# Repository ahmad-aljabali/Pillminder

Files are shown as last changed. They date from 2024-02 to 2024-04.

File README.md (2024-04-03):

# Pillminder
Medication Dispenser and Tracker App. [Download apk](Build/Pillwise.apk)

# Table of Contents
1. [Introduction](#introduction)
2. [Design](#design)
1. [Hardware](#hardware)
2. [Electronics](#electronics)
3. [Mobile App](#app)
3. [Building the App](#building)
4. [Issues and Challenges](#issues)
5. [Conclusion & Future Works](#conclusion)
6. [References](#references)

# Introduction 
In this project, our aim was to develop an inventive solution for monitoring and managing resources vital to an individual's well-being, with a specific focus on medications. Our initial market research highlighted areas for improvement in existing solutions.

We observed that available products in the market were either exclusively app-based or hardware-based. The existing dispensers were often proprietary, offering limited customization options, featuring bulky designs, and were not tailored to meet the needs of individual users.

To address these shortcomings, we chose a dual-component approach for our project: a smart pill dispenser and a companion mobile app designed for medication tracking. Our vision was to create a comprehensive product that could function both independently and in sync with each other. This design allowed users the flexibility to use the dispenser on its own or utilize the app solely as a medication reminder. By providing this dual functionality, our aim was to offer a flexible and user-friendly solution, catering to a diverse range of user preferences and needs.

## Videos

https://github.com/ahmad-aljabali/Pillwise/assets/36141448/d999e439-b2e4-46c4-b8eb-4feb8e34578a

https://github.com/ahmad-aljabali/Pillwise/assets/36141448/cecf2776-79e3-4c20-b9d0-7685703d312a 

# Design 

## Hardware 
The aim was to create a simple and compact design that can be placed and used easily. The design incorporated a rotating plate capable of storing multiple medications, facilitating dispensing according to the prescription. To enhance user interaction, a visual display feature was integrated to notify users of medication times and provide instructions.

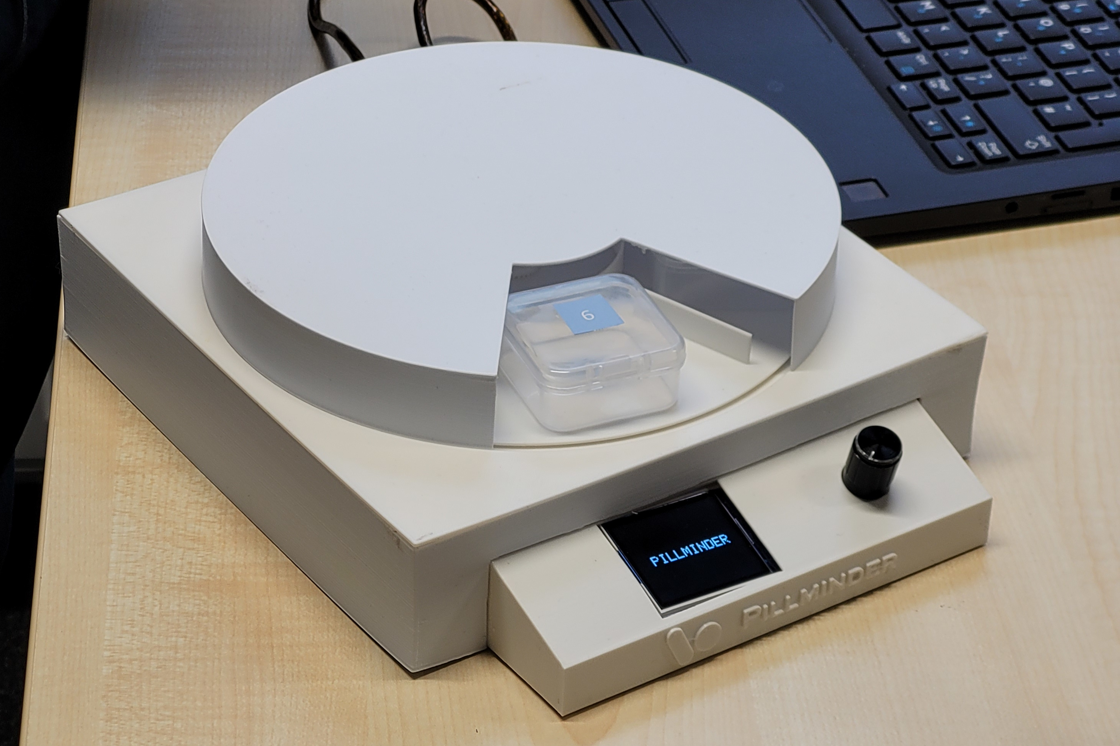
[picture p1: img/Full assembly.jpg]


### 3D Modeling & Printing
The design process was accomplished by:

- Measure the dimensions of the main components so we can build a model that fits all the components and maintains a compact size. Precise measurements were obtained using a digital caliper.

- Using Autodesk Inventor Professional, we created detailed 3D models for each part of the prototype. This design process accounted for the dispenser's functionality, accommodating six types of medication on a rotating plate.

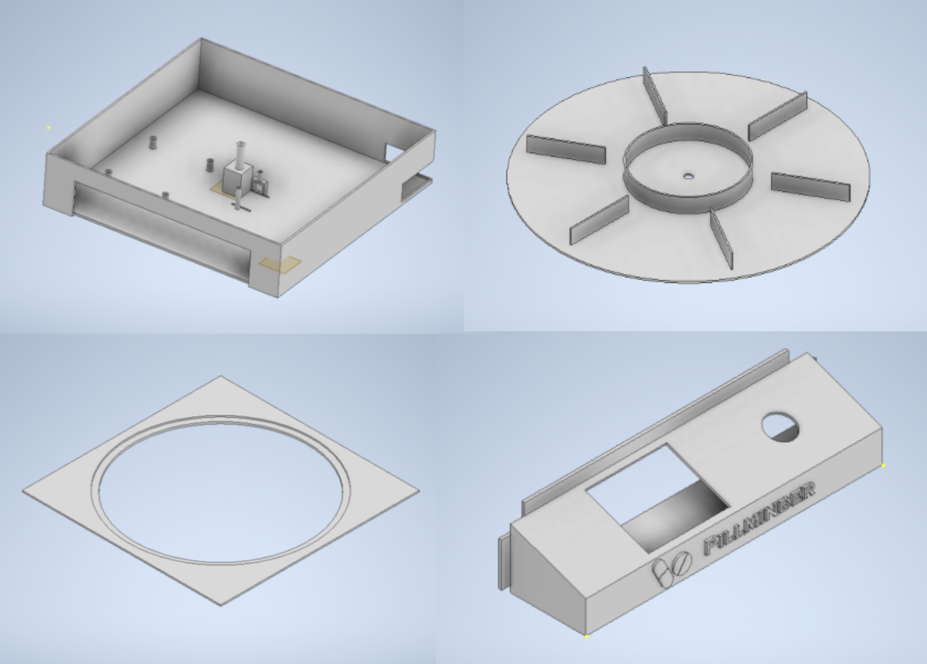
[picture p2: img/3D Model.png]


- The next step involved bringing our 3D models to life. We utilized a Prusa i3 MK3S+ FDM printer, with a slicing size set at 0.2-0.3 mm. The final printed dimensions of the prototype were 21 x 21 x 25 cm.

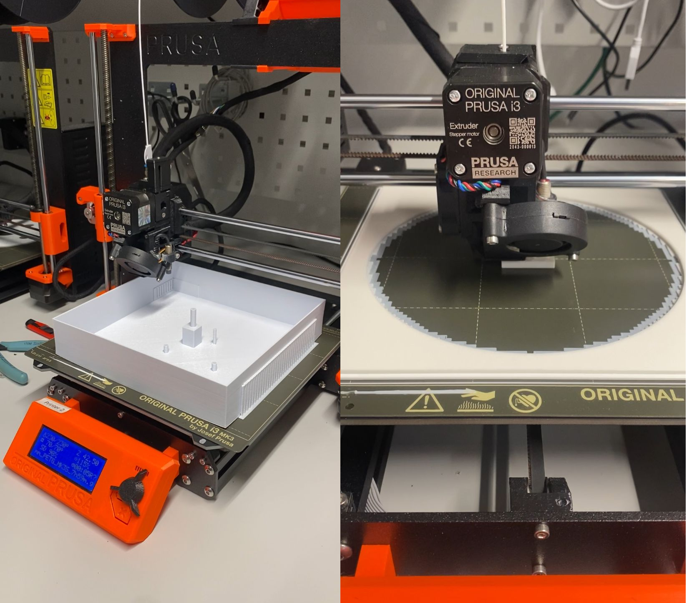
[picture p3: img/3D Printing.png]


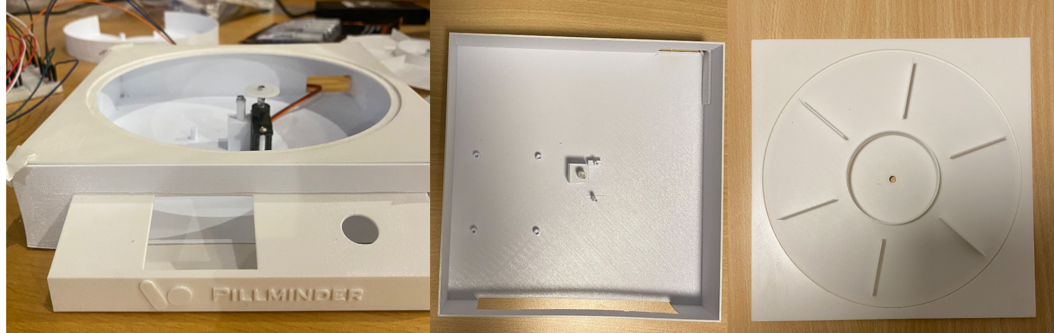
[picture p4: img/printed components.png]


## Electronics 
In this section, we will write in detail about the electronic components that are the core of our prototype. To achieve the goal of creating an automated prototype, we used an Arduino Uno microcontroller as the central processing unit. To establish a connection between the Arduino Uno and our mobile application, we integrated the ESP8266-01 Wi-Fi module. This module served as the communication bridge, enabling real-time interaction between the prototype and the user through the mobile app.

### Electronic Component:
- Arduino Uno
- WiFi ESP8266-01S
- Servo Motor MF-90
- Rotary Encoder KY-040
- LCD 1.8" TFT Display ST7735S
- Wires & Breadboard

After having every component , we started to verified the functionality of them before integrating into the overall electronic system.

https://github.com/ahmad-aljabali/Pillwise/assets/36141448/dc6bbddc-dbca-42d1-aa9b-e82a9cc1dbc5

## Mobile App 
### Architecture & Libraries
The app was develop with the goal of being usable as a standalone medicine tracking mobile app and/or in combination with the Dispenser.

Another design consideration was to use cross platform technologies, we settled in the end on using React single page PWA framework because of our prior familiarity with web development, this was used in combination with Ionic and Capacitor to add native app functionality.

For management of native functionality the following capacitor add-ons were utilized:
- Filesystem[^5]: for storing and reading user data locally 
- Local Notification[^6]: to provide push notification to user

For ease of development and quick modification the user data is stored in JSON format instead of using a dedicated database, saved in the standard native Android file structure.

### Layout
The app is split into three main screens, each displaying the following.
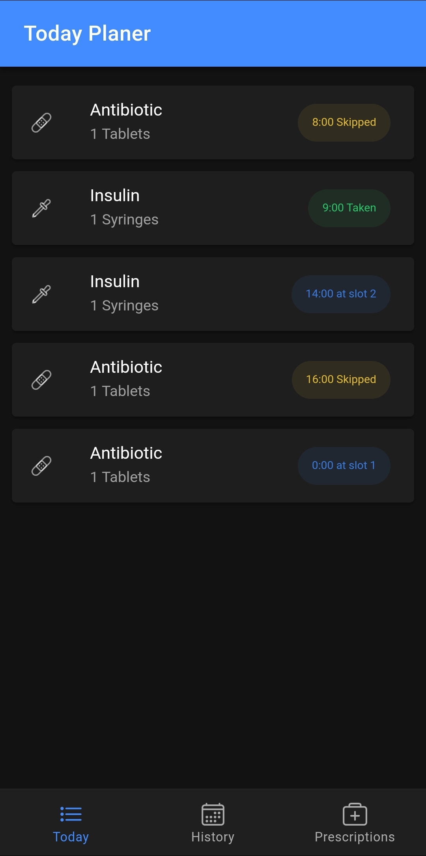
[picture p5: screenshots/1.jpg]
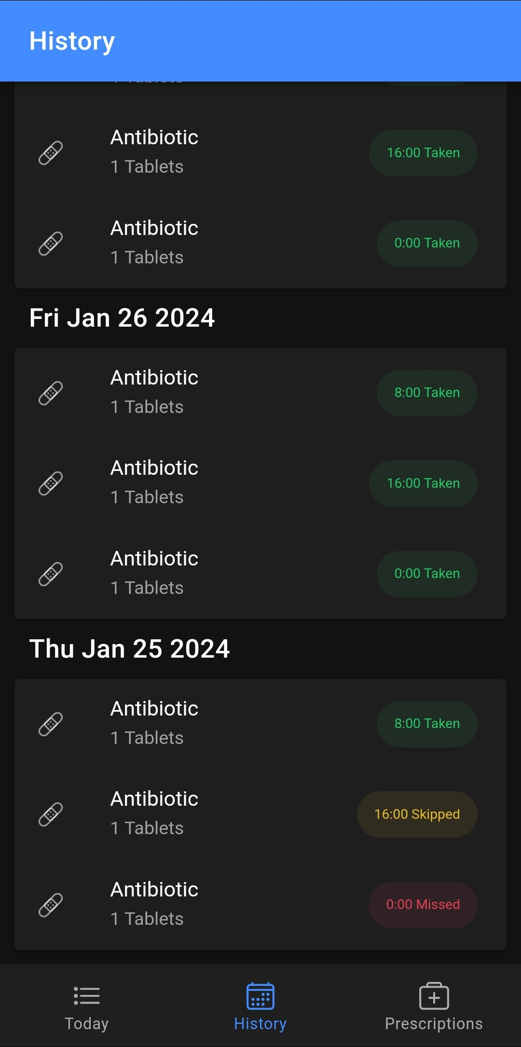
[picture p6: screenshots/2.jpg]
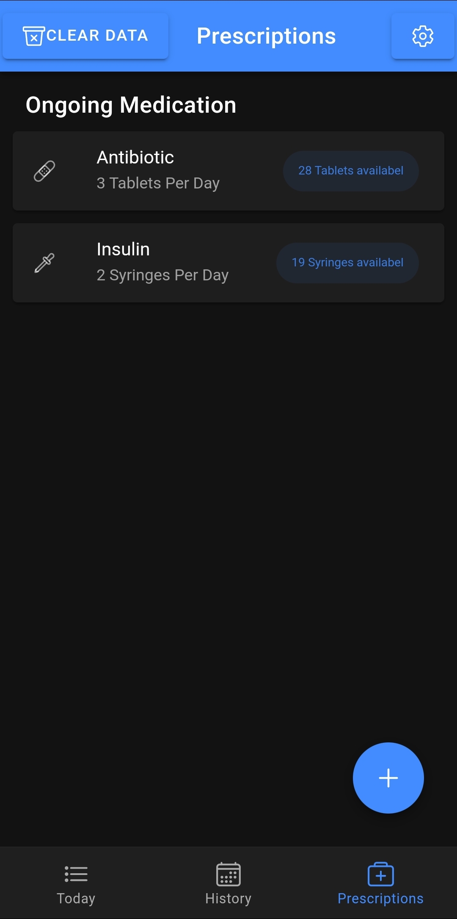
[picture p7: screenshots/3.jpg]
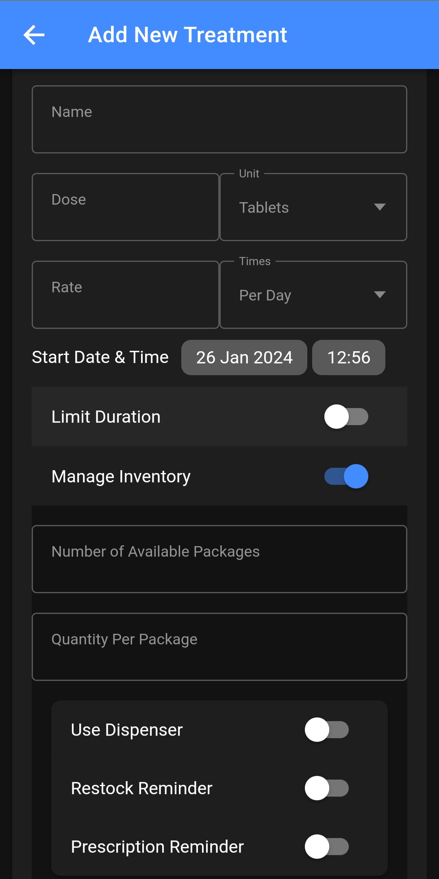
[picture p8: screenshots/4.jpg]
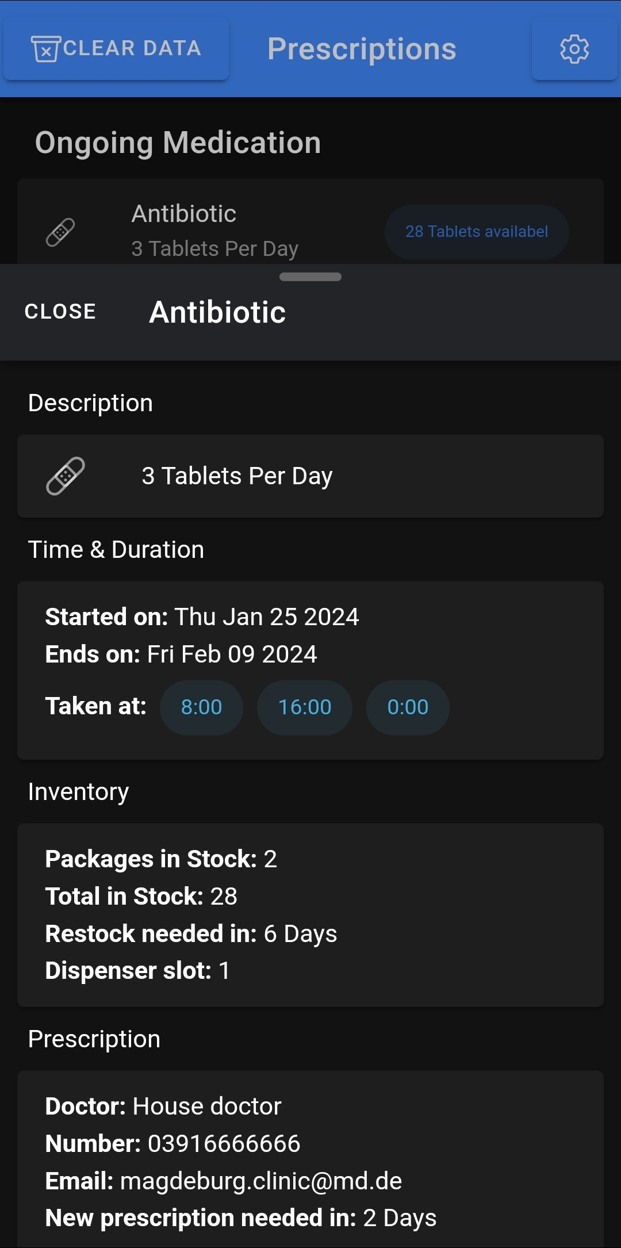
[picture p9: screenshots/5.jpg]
||||
---|---|---|---|---

**Today**
- Medication Name, Dose, Type
- Times to be taken today
- Slot if they're stored in Dispenser
- Allow user to Confirm or Skip medicine

**History**
- Status Record of Medication in previous days

**Prescriptions**
- Active Prescriptions
- Current stock value
- Button to add new prescription

Additionally the following screens are available.

**Add New Treatment**
- Form to Add New Medication
- Name, Dose, Type, Rate, Start Date & Time
- Inventory Info
- Prescription and Doctor Info

**Medicine Details**
- Can be accessed by clicking on Medication in Prescriptions Screen
- Shows complete medication info

# Building the App 
To build the App from the available source code [^7] use the below instructions.

### Install Dependencies
```
npm install
```

### Run locally
```
ionic serve
```
### Build for android
```
ionic cap add android
ionic cap build android
```
**_Then build using android studio_**
**_Replace android with ios and use Xcode to build for ios_**

# Issues and Challanges 

## 3D Printing

The 3D printer's dimensions posed a challenge as they were smaller than the model dimensions. Consequently, we divided the case into two parts one for internal components and another for the LCD and encoder. 

Securing all components proved challenging, especially when considering the rotating plate where precision was crucial. The plate needed to be affixed with a glued gear, ensuring contact with the servo but not overly tight. Excessive tightness could hinder the servo motor's smooth rotation, leading to potential interruptions. 

Addressing this challenge would require creating a new model with more accurate dimensions and improved fixation points, resolving potential issues related to plate movement and servo rotation.

However, due to time limitations and restricted access to the printing lab, this optimization was not implemented.

## Electronics

Our initial microcontroller choice was Raspberry Pi, because of its communication capabilities and the ease of hosting a local server.

Unfortunately, the Raspberry Pi unexpectedly ceased functioning, causing the need for an alternative solution. The simplest idea was to buy another Raspberry Pi, but out limited budget led us to look for a more affordable solution. Since most of us were familiar with Arduino Uno, we decided to use it as our microcontroller. 

We knew that Arduino Uno does not have built-in Wi-Fi, we solved this limitation by adding the ESP8266-01 module. This decision was influenced by the compact size of the ESP8266-01, which fit with the dimensions of our pre-existing 3D printed model. Despite the ESP8266-01's benefits, we faced some challenges due to its basic low level functionality, forcing us to use "_AT Commands_" instead of standard libraries. 

This method worked well, but it required a lot of effort to handel and parse incoming command, due to lack of libraries to handel requests for this module.

# Conclusion & Future Works 
Our project began with a basic idea: creating a prototype for a medical dispenser paired with a mobile app. We simultaneously worked on prototyping, 3D modeling, Arduino Uno code, and mobile app. Despite facing various challenges, we successfully integrated the dispenser prototype with the mobile app, simplifying medication tracking for users.

Looking ahead, the design may be improved by enhancing user-friendliness. This involves implementing a database of nearby pharmacies with specific medicines and introducing a scanning feature for users to easily input medication details into the app. These improvements will provide users with a more intuitive and efficient medication management experience.

# References 
[^1]: https://www.electronics-lab.com/project/using-st7735-1-8-color-tft-display-arduino/
[^2]: https://gndtovcc.home.blog/2020/02/11/code-for-obtaining-ip-address-from-esp-01/
[^3]: https://www.makerguides.com/servo-arduino-tutorial/
[^4]: https://www.diyengineers.com/2021/06/03/arduino-rotary-encoder-how-to-use/
[^5]: https://capacitorjs.com/docs/apis/filesystem
[^6]: https://capacitorjs.com/docs/apis/local-notifications
[^7]: https://github.com/ahmad-aljabali/Pillwise/tree/main/App%20src%20code

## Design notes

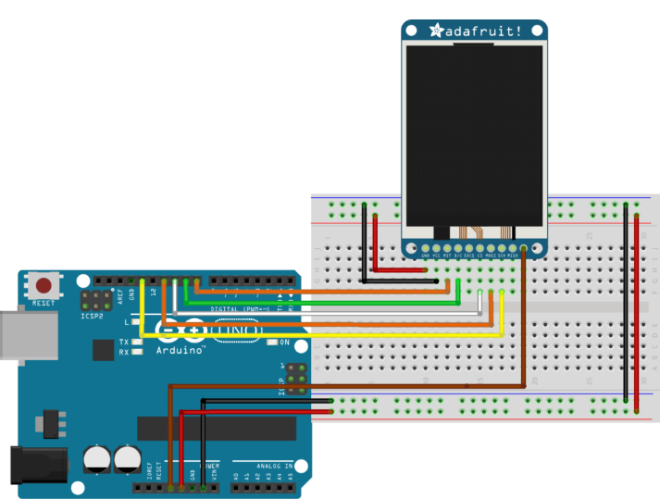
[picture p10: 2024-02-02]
img/image.png

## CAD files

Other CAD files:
3D Models/Box cover.ipt
3D Models/Box.ipt
3D Models/Plate cover.ipt
3D Models/Rotating Plate.ipt
3D Models/Screen1.ipt

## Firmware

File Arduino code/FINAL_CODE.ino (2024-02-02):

#include <SPI.h>
#include <Adafruit_GFX.h>
#include <Adafruit_ST7735.h>
#include <Servo.h>
#include <SoftwareSerial.h>

Adafruit_ST7735 tft = Adafruit_ST7735(10, 9, 8); // (CS, DC, RST)
Servo myservo;

#define encoderOutA 6 // CLK pin of Rotary Encoder
#define encoderOutB 7 // DT pin of Rotary Encoder
#define buttonPin 5    // Push-button pin
#define servoPin 4    // Servo control pin

SoftwareSerial ESP8266(3, 2);
const int arraySlot[7] = {80,93, 108, 123, 138, 153,180};
String names[7];
unsigned char times_check=0;
unsigned char check_connection=0;  
int counter ;// shife
int presentState;
int previousState;
int lastButtonState = HIGH;
int buttonState;
unsigned long lastDebounceTime = 0;
unsigned long debounceDelay = 50;
bool medicineTaken = false;
bool medicinePutted = false;
int i;
String secondValueName="";
String espData = "";
int slotValue=-1;
int typeValue;
void setup() {
  Serial.print(arraySlot[1]);
  pinMode(encoderOutA, INPUT);
  pinMode(encoderOutB, INPUT);
  pinMode(buttonPin, INPUT_PULLUP); // Enable internal pull-up resistor for the button pin

  myservo.attach(servoPin);

  tft.initR(INITR_GREENTAB);
  tft.setRotation(1);

  Serial.begin(115200);
  ESP8266.begin(115200);
  Serial.println("rjeu");
ESP8266.print("***VER:");
delay(2000);
ESP8266.println("AT+RST");
delay(3000);
ESP8266.println("AT+CWQAP");
delay(1000);
ESP8266.println("AT+GMR");
delay(1000);
ESP8266.println("AT+CWMODE=3");
delay(1000);
ESP8266.println("AT+CWLAP");
delay(3000);
ESP8266.println("AT+CIPMUX=1"); // Set multiple connections mode
delay(1000);
ESP8266.println("AT+CIPSERVER=1,80");
delay(10000);
Serial.println("Connecting to Wifi");
ESP8266.print("AT+CWJAP=\"Klevis\",\"klevis2023\"\r\n");
delay(10000);
     

 // setupESP8266();

  previousState = digitalRead(encoderOutA);
  //Serial.print(previousState);// just to see what print in beging 
}

void loop() {
  handleEsp8266();
  moveEncoder();
  checkButton();
  
}

void connectToWifi() {
  Serial.println("Connecting to Wifi");
while(check_connection==0)
  {
    Serial.print(".");
    ESP8266.print("AT+CWJAP=\"Klevis\",\"klevis2023\"\r\n");
    ESP8266.setTimeout(5000);
     if(ESP8266.find("WIFI CONNECTED\r\n")==1)
      {
      Serial.println("WIFI CONNECTED");
      int variabbb=1;
      break;}
      times_check++;
     if(times_check>3) {
      times_check=0;
      Serial.println("Trying to Reconnect..");}
}}





void setupESP8266() {
  ESP8266.println("AT+CIPMUX=1"); // Set multiple connections mode
  delay(1000);
  ESP8266.println("AT+CIPSERVER=1,80");
  delay(1000);
}

void handleEsp8266() {
  while (ESP8266.available()) {
    char c = ESP8266.read();
    espData += c;
    //Serial.print(espData);
    if (c == '\n') {
      String result = extractSubstring(espData, ":GET /", "2520");
      if (result.length() > 0) {
        String firstValueType = extractSubstring(result, "?type=", "$");
        secondValueName = extractSubstring(result, "$name=", "&");
        String thirdValueSlot = extractSubstring(result, "&slot=", "%");

        Serial.println("Received Values:");
        Serial.println("Type: " + firstValueType);
        Serial.println("Name: " + secondValueName);
        Serial.println("Slot: " + thirdValueSlot);
        slotValue = thirdValueSlot.toInt();
        typeValue=firstValueType.toInt();
        names[slotValue]=secondValueName;

        espData = "";
        firstValueType = "";
        secondValueName = "";
        thirdValueSlot = "";
        result = "";
        //slotValue=-1;
      }
    } 
    /*
    else {
      espData += c;
    }*/
  }
}

void moveServoBasedOnSlot(int slotValue) {
  // Implement your servo movement logic based on the slot value
  int angle = map(slotValue, 0, 100, 0, 180); // Adjust the mapping as needed
  myservo.write(angle);
  delay(500); // Adjust delay as needed
}

void printToLCD(String message) {
  tft.fillScreen(ST77XX_BLACK);
  tft.setCursor(10, 20);
  tft.setTextSize(2);
  tft.setTextColor(ST77XX_WHITE);
  tft.print("Name: ");
  tft.print(message);
}

String extractSubstring(const String &input, const String &startKeyword, const String &endKeyword) {
  int startIndex = input.indexOf(startKeyword);
  int endIndex = input.indexOf(endKeyword, startIndex + startKeyword.length());

  if (startIndex != -1 && endIndex != -1) {
    return input.substring(startIndex + startKeyword.length(), endIndex);
  } else {
    return ""; // Return an empty string if either start or end keyword is not found
  }
}

void checkButton() {
  int reading = digitalRead(buttonPin);

  if (reading != lastButtonState) {
    lastDebounceTime = millis();
  }

  if ((millis() - lastDebounceTime) > debounceDelay) {
    if (reading != buttonState) {
      buttonState = reading;

      if (buttonState == LOW  && slotValue==-1) {
        tft.fillScreen(0);
        tft.setCursor(50,60);
        tft.print("WAIT");
        servo_Slot(counter);
        tft.fillScreen(0); 
        tft.fillScreen(ST77XX_BLACK);
  tft.setCursor(10, 40);
  tft.setTextSize(2);
  tft.setTextColor(ST77XX_WHITE);
  tft.print("medicine");
  tft.setCursor(10, 20);
  tft.print("Take the");
  tft.setCursor(10, 60);
  tft.print(names[counter]);
  Serial.print(names[counter]);
  Serial.print("the slot");
  Serial.print(counter);
  delay(3000);
  tft.fillScreen(0); 
  tft.setCursor(23, 60);
   tft.print("PILLMINDER");
      }
      if(buttonState==LOW && slotValue!=-1){
        if(typeValue==1){
          tft.fillScreen(0);
          tft.setCursor(30,60);
          tft.print("WAIT");
          servo_Slot(slotValue);
          
          tft.fillScreen(0); 
  //displayMessage("Take the");
  tft.fillScreen(ST77XX_BLACK);
  tft.setCursor(10, 40);
  tft.setTextSize(2);
  tft.setTextColor(ST77XX_WHITE);
  tft.print("medicine");
  tft.setCursor(10, 20);
  tft.print("Take the");
  tft.setCursor(10, 60);
  tft.print(names[slotValue]);
  Serial.print(names[slotValue]);
  Serial.print("the slot");
  Serial.print(slotValue);
  delay(3000);
  tft.fillScreen(0); 
  tft.setCursor(10, 40);
   tft.print("PILLMINDER");
   slotValue=-1;
       }
       else {
        tft.fillScreen(0);
        tft.fillScreen(ST77XX_BLACK);
        tft.setTextSize(2);
       tft.setCursor(30,60);
          tft.print("WAIT");
          servo_Slot(slotValue);
          
          tft.fillScreen(0); 
  //displayMessage("Take the");
  tft.fillScreen(ST77XX_BLACK);
  tft.setCursor(10, 40);
  tft.setTextSize(2);
  tft.setTextColor(ST77XX_WHITE);
  tft.print("medicine");
  tft.setCursor(10, 20);
  tft.print("Put the");
  tft.setCursor(10, 60);
  tft.print(names[slotValue]);
  
  Serial.print(names[slotValue]);
  Serial.print("the slot");
  Serial.print(slotValue);
  delay(3000);
  tft.fillScreen(0); 
  tft.setCursor(10, 40);
   tft.print("PILLMINDER");
   slotValue=-1;
       }
       
      }
    }
  }

  lastButtonState = reading;
}

void moveEncoder() { //in here just you take the nb of slot
  presentState = digitalRead(encoderOutA);
  if (presentState != previousState) {
    if (digitalRead(encoderOutB) != presentState) {
      counter++;
      if (counter > 6) {
        counter = 1;
      }
    } else {
      counter--;
      if (counter < 1) {
        counter = 6;
      }
    }
    Serial.print("Position: ");
    Serial.println(counter);

    tft.fillScreen(ST77XX_BLACK);
    tft.setCursor(10, 20);
    tft.setTextSize(2);
    tft.setTextColor(ST77XX_WHITE);
    tft.print("Slot:");
    tft.print(counter);
  }
  previousState = presentState;
}

void moveServoBasedOnCounter(int counterValue) {
  int angle = calculateServoAngle(counterValue);
  myservo.write(angle);
  delay(500); // Delay to allow the servo to reach the desired position
}
int calculateServoAngle(int counterValue) {// change this with our angel
  //int maxAngle = 180;
  //int steps = 6; // Assuming 5 steps
  int targetAngle = 15* counterValue + 93;
  return targetAngle;
}

void displayMessage(String message) {
  tft.fillScreen(ST77XX_BLACK);
  tft.setCursor(10, 20);
  tft.setTextSize(2);
  tft.setTextColor(ST77XX_WHITE);
  tft.print(message);
}

void servo_Slot(int angel){// is the slot 
  int ReadAngel=myservo.read();
  if (arraySlot[angel-1]<ReadAngel){
  //displayMessage("Wait"); 

    for ( i=ReadAngel; i>arraySlot[angel]; i -= 1) {
    myservo.write(i);  // Move the servo to the current angle
    Serial.println(i);
    delay(50);
  } //tft.fillScreen(0);
  //displayMessage("Take the medicine"+ secondValueName);
  }
  else {
    //displayMessage("Wait"); 
  for ( i=ReadAngel; i<arraySlot[angel]; i += 1) {
    myservo.write(i);  // Move the servo to the current angle
    Serial.println(i);
    delay(50);
  }
  /* 
  tft.fillScreen(0); 
  //displayMessage("Take the");
  tft.fillScreen(ST77XX_BLACK);
  tft.setCursor(10, 40);
  tft.setTextSize(2);
  tft.setTextColor(ST77XX_WHITE);
  tft.print("medicine");
  tft.setCursor(10, 20);
  tft.print("take the");
  tft.setCursor(10, 60);
  tft.print(names[angel]);
  Serial.print(names[angel]);
  Serial.print("the angel");
  Serial.print(angel); */
}
}

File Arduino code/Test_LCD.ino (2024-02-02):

#include <SPI.h>
#include <Adafruit_GFX.h>    // Core graphics library
#include <Adafruit_ST7735.h> // Hardware-specific library

#define TFT_CS        A2
#define TFT_RST        A1// Or set to -1 and connect to Arduino RESET pin
#define TFT_DC         A0

Adafruit_ST7735 tft = Adafruit_ST7735(TFT_CS, TFT_DC, TFT_RST);

void setup(void) {
  pinMode(7, LOW);
  tft.initR(INITR_144GREENTAB); // Init ST7735R chip, green tab
  tft.setRotation(0); // set display orientation 
  pinMode(7, LOW);
}

void loop() {
  tft.fillScreen(ST77XX_CYAN);
  print_text(25,30,"HELLO",3,ST7735_WHITE);
  print_text(20,70,"WORD!",3,ST7735_BLUE);
  delay(5000);
  pinMode(7, HIGH);
  delay(1000);
  pinMode(7, LOW);
  tft.fillScreen(ST77XX_BLACK);
  tft.fillRoundRect(25, 10, 78, 60, 8, ST77XX_WHITE);
  tft.fillTriangle(42, 20, 42, 60, 90, 40, ST77XX_RED);
  delay(5000);
  
  tft.fillScreen(ST77XX_CYAN);
  tft.drawRect(5,5,120,120,ST77XX_RED);
  tft.drawFastHLine(5,60,120,ST77XX_RED);
  tft.drawFastVLine(60,5,120,ST77XX_RED);
  delay(5000);
}

void print_text(byte x_pos, byte y_pos, char *text, byte text_size, uint16_t color) {
  tft.setCursor(x_pos, y_pos);
  tft.setTextSize(text_size);
  tft.setTextColor(color);
  tft.setTextWrap(true);
  tft.print(text);
}

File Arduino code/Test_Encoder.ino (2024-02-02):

 #define encoderOutA 5 // CLK pin of Rotary Enocoder
 #define encoderOutB 4 // DT pin of Rotary Enocoder
 
 int counter = 0; 
 int presentState;
 int previousState;  
 void setup() { 
   pinMode (encoderOutA,INPUT);
   pinMode (encoderOutB,INPUT);
   
   Serial.begin (115200);
      previousState = digitalRead(encoderOutA);   // Get current state of the encoderOutA
 } 
 void loop() { 
   presentState = digitalRead(encoderOutA); 
      if (presentState != previousState)
      {     
          if (digitalRead(encoderOutB) != presentState) 
          { 
       counter ++;
     } 
     else {
       counter --;
     }
     Serial.print("Position: ");
     Serial.println(counter);
   } 
   previousState = presentState; // Replace previous state of the encoderOutA with the current state
 }

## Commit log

2024-02-02 Adding CAD Inventor files
    [Box cover.ipt, Box.ipt, Plate cover.ipt, Rotating Plate.ipt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]
2024-02-02 Add assembled electronics video
